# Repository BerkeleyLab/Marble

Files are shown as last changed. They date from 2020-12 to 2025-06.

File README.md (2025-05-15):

# Marble board

Marble is a dual FMC FPGA carrier board developed for general purpose use in particle accelerator electronics instrumentation. It is currently under development and the base platform for two accelerator projects at DOE: ALS-U (the Advanced Light Source Upgrade at LBNL) and LCLS-II HE (the Linac Coherent Light Source II High Energy upgrade).

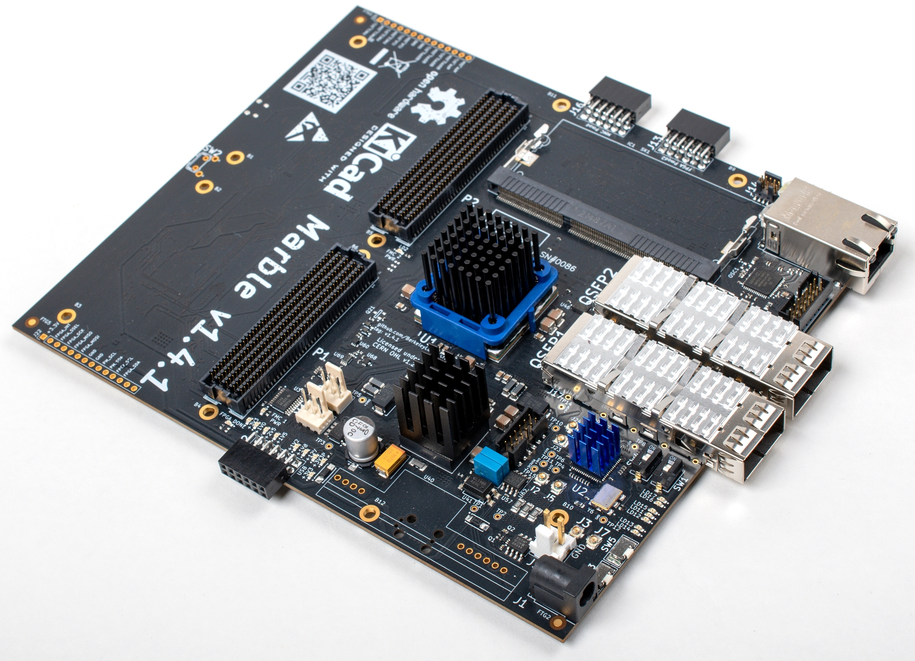
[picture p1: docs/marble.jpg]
marble

_Photo Credit: Thor Swift/LBNL_

The design responds to deployment needs in an accelerator environment: reliability, ability to be remotely programmed, safety watchdog, self monitoring, etc. It is intended to be the base digital design for instrumentation electronics, with the capability of connecting to different I/O or analog front ends through the FMC connectors. It targets cost-effectiveness for deployments of hundreds of units. It is based on a Network Attached Device (NAD) approach, where high-speed serial links serve as the communication backbone with other systems in the accelerator.

## Basic Idea

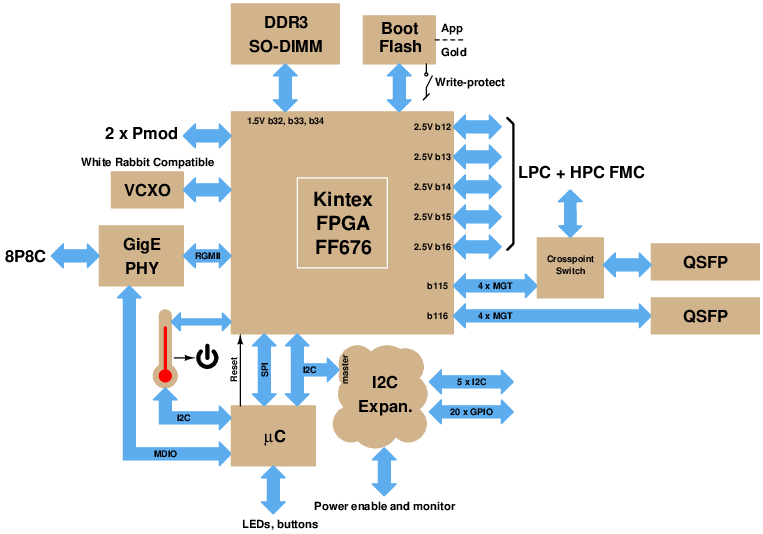
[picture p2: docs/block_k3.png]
block diagram


## Tools

The Marble design is fully Open Source (licensed under the CERN Open Hardware License v1.2) and designed using Open Source tools.

The schematic/layout tool used is [KiCad EDA](http://www.kicad.org/)
version 6.0.11; maybe you can use other versions in the 6.0.x series
(Marble design versions 1.3 and before used KiCad 5.0.x).
Other versions will very likely either not read the files
in this repo, or will save files that are not compatible with
collaborators' reference installations.
We also make use of [KiBoM](https://github.com/SchrodingersGat/KiBoM).

See more comments about KiCad versions in [design/scripts/README.md](design/scripts/README.md).

## Major Parts

* U1: Xilinx [XC7K160T-FFG676](https://www.xilinx.com/products/silicon-devices/fpga/kintex-7.html) FPGA
* SK1: 204-pin [DDR3](https://en.wikipedia.org/wiki/DDR3_SDRAM) [SO-DIMM](https://en.wikipedia.org/wiki/SO-DIMM)
* U54: ST [STM32F207VCT6](http://www.st.com/st-web-ui/static/active/en/resource/technical/document/datasheet/CD00237391.pdf) Microcontroller
* U4: Marvell [88E1512](https://www.marvell.com/documents/eoxwrbluvwybgxvagkkf/) Ethernet PHY
* U20: TI [CDCM61004](http://www.ti.com/product/CDCM61004) Clock Generator
* U23: FTDI [FT4232H-56Q](https://www.ftdichip.com/Products/ICs/FT4232H.htm) USB interface
* U35: Analog Devices [LTM4673](https://www.analog.com/en/products/ltm4673.html) Quad Output Voltage Regulator Module
* Y1: Taitien [TXEAADSANF-25.000000](https://www.taitien.com/wp-content/uploads/2015/12/XO-0076_TX.pdf) 25 MHz VCTCXO

## Documentation

Documentation is available in the [Marble documentation page](https://berkeleylab.github.io/Marble/manuals.html).

If you have a physical board that has already been tested you can jump directly to the User Guide. If you need to qualify, test, or troubleshoot a board, you can use the fabrication acceptance test guide. These documents are also available as artifacts for each fabrication release.

Other documentation includes notes on the board's [current measurement capabilities](docs/shunts.md).

## Manufacturing package and other scripted processes

The Marble design source files, along with documentation, are available in this repository under version control.
Other non-source artifacts (such as fabrication packages) are available for download for each manufactured release.
If you would like to manufacture Marble boards from any of the released version, download the manufacturing package for that particular version from the list of artifacts and request a quote from your favorite vendor. Marble is not yet available as a catalog item from any of our manufacturing partners.

When a new design version of Marble is ready for manufacture, a release is tagged in this repository and the corresponding artifacts are made available for download (e.g. manufacturing package, documentation, etc.). The physical boards have a [QR code](https://en.wikipedia.org/wiki/QR_code) on them, pointing to the board's tagged release on GitHub so a physical board can be mapped to the source code and fabrication package used for its manufacture.

Updating the QR code for a new release, updating the silkscreen design accordingly and generating a fabrication package is a process in itself. That and other processes are partially scripted. Additional information on those processes and the scripts used can be found in the [scripts subdirectory](design/scripts). A [README](design/scripts/README.md) covers the following:

* Inserting QR code on silkcsreen
* Generating artifacts for manufacturing
* Generating Xilinx constraint file
* Updating the I2C subsystem diagram in schematics

## Credits

The initial design work was supported by the Berkeley Accelerator Controls and Instrumentation (BACI), a DOE High Energy Physics (HEP) General Accelerator R&D (GARD) program and carried out by the Accelerator Technology Group (ATG) at LBNL, in collaboration with the Warsaw University of Technology (WUT) and Creotech Instruments in Poland.

The board was designed by Michal Gaska (WUT), and Larry Doolittle (LBNL) is the mastermind behind the design. Michael Betz, Vamsi Vytla, Sergio Paiagua, Eric Norum, Shree Murthy, and Keith Penney (LBNL) have also contributed to the design and supporting software and firmware throughout the development.

## Copyright

Marble Copyright (c) 2019-2023, The Regents of the University of California, through Lawrence Berkeley National Laboratory (subject to receipt of any required approvals from the U.S. Department of Energy). All rights reserved.

This documentation describes Marble and is licensed under the [CERN OHL v1.2](https://ohwr.org/project/licences/wikis/cern-ohl-v1.2).

NOTICE. This documentation was developed under funding from the U.S. Department of Energy and the U.S. Government consequently retains certain rights. As such, the U.S. Government has been granted for itself and others acting on its behalf a paid-up, nonexclusive, irrevocable, worldwide license in the documentation to reproduce, distribute copies to the public, prepare derivative works, and perform publicly and display publicly, and to permit others to do so.

You may redistribute and modify this documentation under the terms of the CERN OHL v.1.2. (http://ohwr.org/cernohl). THIS DOCUMENTATION IS PROVIDED BY THE COPYRIGHT HOLDERS AND CONTRIBUTORS "AS IS" AND ANY EXPRESS OR IMPLIED WARRANTIES, INCLUDING, BUT NOT LIMITED TO, THE IMPLIED WARRANTIES OF MERCHANTABILITY AND FITNESS FOR A PARTICULAR PURPOSE ARE DISCLAIMED. IN NO EVENT SHALL THE COPYRIGHT OWNER OR CONTRIBUTORS BE LIABLE FOR ANY DIRECT, INDIRECT, INCIDENTAL, SPECIAL, EXEMPLARY, OR CONSEQUENTIAL DAMAGES (INCLUDING, BUT NOT LIMITED TO, PROCUREMENT OF SUBSTITUTE GOODS OR SERVICES; LOSS OF USE, DATA, OR PROFITS; OR BUSINESS INTERRUPTION) HOWEVER CAUSED AND ON ANY THEORY OF LIABILITY, WHETHER IN CONTRACT, STRICT LIABILITY, OR TORT (INCLUDING NEGLIGENCE OR OTHERWISE) ARISING IN ANY WAY OUT OF THE USE OF THIS SOFTWARE, EVEN IF ADVISED OF THE POSSIBILITY OF SUCH DAMAGE. Please see the CERN OHL v.1.2 for applicable conditions.

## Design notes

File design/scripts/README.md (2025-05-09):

# Marble board scripting and processes

When a new design version of Marble is ready for manufacture, a release is tagged in this repository and the corresponding artifacts are made available for download (e.g. manufacturing package, documentation, etc.). We want the physical boards to have a [QR code](https://en.wikipedia.org/wiki/QR_code) on them, pointing to the board's tagged release on GitHub.  This way a physical board can be mapped to the source code and fabrication package that was used for its manufacture.

Updating the QR code for a new release, updating the silkscreen design accordingly and generating a fabrication package is a process in itself. That and other processes are partially scripted and documented here.

## Generating the manufacturing package

If you have made changes to the Marble design and are ready to generate the manufacturing package, the first step is to pick a version number for the new release. The current version is `v1.4.4`.

### Required software

* [KiCad](https://www.kicad.org/): version 6.0.x (x &ge; 9)
* [KiBoM](https://github.com/SchrodingersGat/KiBoM): version 1.9.1
* [KiAuto](https://github.com/INTI-CMNB/KiAuto): version 2.2.1

KiCad version 6 is needed.
We hope this still supports [reproducible](https://reproducible-builds.org) fabrication package builds. This means byte-for-byte identical zip files, independent of which person and computer runs the process.

### Update the QR code on the silkscreen

The QR code needs to be re-generated so it points to the new version release. To update the URL, edit the Python script used to generate the QR code image: `design/scripts/qr_create.py`. The URL in that file pointing to the current release is: <https://github.com/BerkeleyLab/Marble/releases/tag/v1.4.4>.

From the design directory, run the Python script:
```console
$ python scripts/qr_create.py
```
That will create a `mm_qr.png` file, which you should be able to preview and
scan with your phone to confirm it has the intended link.

Open the KiCad project: `design/Marble.kicad_pro`

Open the `Bitmap to Component Converter` clicking on this button at the top of the screen:

Bitmap to Component Converter

Click on `Load Bitmap` and select the `mm_qr.png` that you just generated with the Python script. Choose 400 x 400 DPI to get a 19.8 mm output size. Check the `Negative` and `Front silk screen`, click `Export to File` and select `logos/QR.kicad_mod` to replace the previous QR code with the new one. You can now close the `Bitmap to Component Converter` and insert the QR code into the silkscreen.

Open the `PCB Layout Editor` clicking on this button at the top of the screen:

Pcbnew

Press the `b` key to fill copper planes (completing connectivity and getting rid of rats-nest visual clutter), and unselect every layer on the right-hand side except for `F.Silkscreen`.  There's a nice "Hide All Layers" feature available by right-clicking on the layer list.

Select the QR code, right click and select `Update footprint...`. Click `Update` and `Close`.  Now you can check again with your phone, and save the design.

The above instructions are tested with KiCad 6.0.11. Be aware of KiCad issue [#6514](https://gitlab.com/kicad/code/kicad/-/issues/6514). If the results look corrupted and you are not able to scan the QR code from the PCB layout editor, select `Modern Toolset (Fallback)` under KiCad Preferences.

### Generate the manufacturing package

Now that you have the updated QR code on the silkscreen, we're ready to generate the manufacturing package. The process is summarized in the diagram below.

The current design does unfortunately have a baseline of four DRC errors:  overlapping courtyards of part pairs (U57, U62), (U32, U64), (U17, U63) and copper edge clearance for J10.
These are INA219 chips with two package options supported with two (overlapping) footprints.

From the `design` directory, run:

```console
$ bash scripts/manufacturing.sh
```

If everything worked out correctly, the script should have generated the fabrication package in a zipped archive containing the usual manufacturing files for both
PCB fabrication and turn-key assembly:
* Gerber
* Drill
* IPC-D-356
* Board stackup
* BoM
* X-Y placement
* Schematics

The above process is summarized in the diagram below.

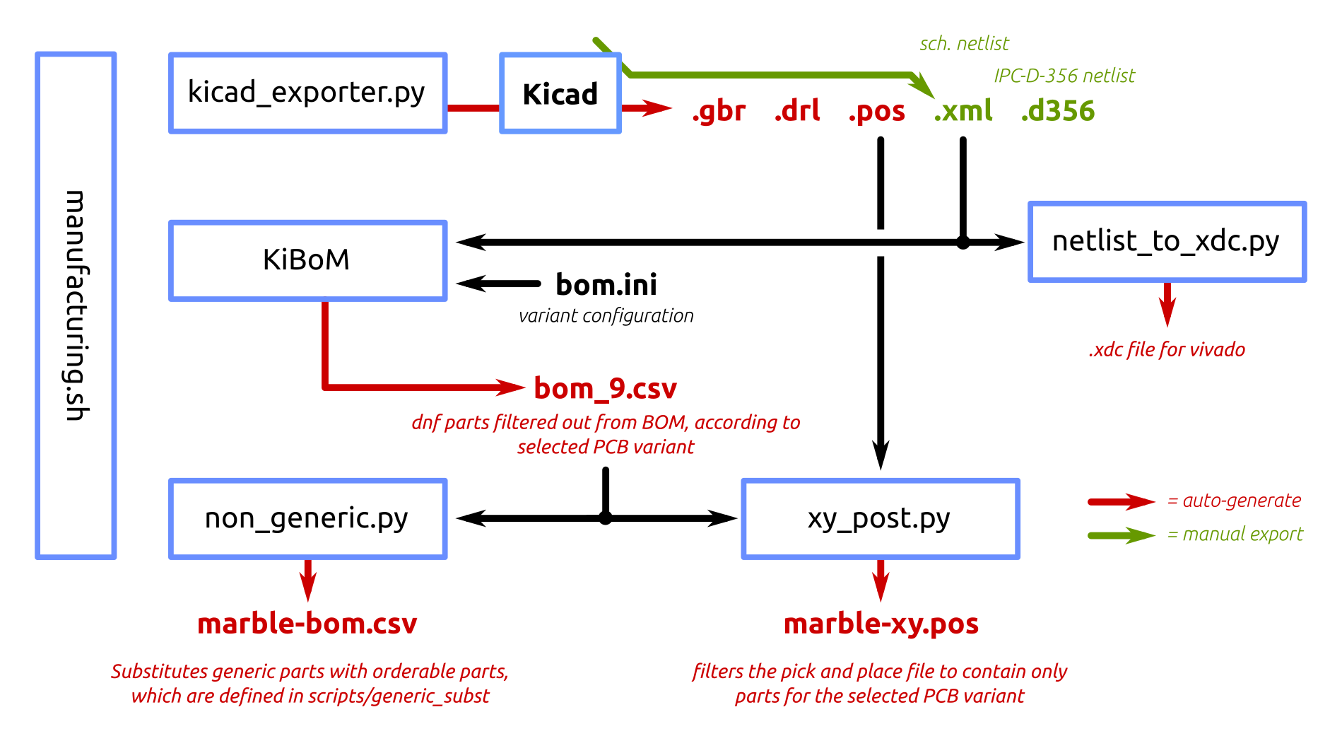
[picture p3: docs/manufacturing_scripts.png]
process


## Xilinx constraint file

A somewhat specialized tool is available to create an XDC file for the Marble design,
based on a netlist file exported from KiCad.

From KiCad (version 6.0.x), open the `Schematic Layout Editor` clicking on this button at the top of the screen:

Pcbnew

* From the top menu, select `File / Export /  Netlist`
* Select the `OrcadPCB2 tab`, click on `Export Netlist` and `Save`. The result shows up as `Marble.net`
* If the above netlist was saved in the `design` directory, from the command line run:
```console
$ python3 scripts/netlist_to_xdc.py Marble.net
```

The result shows up as `Marble.xdc`, which can be used for your FPGA designs.

## Update I2C subsystem diagram in schematics

Run the following command from the top level directory before importing the I2C subsystem diagram into the `I2C_MUX.sch` schematic:
```console
$ convert docs/marble2_i2c.eps -scale 1840 marble2_i2c.png
```
where `convert` is part of [ImageMagick](https://en.wikipedia.org/wiki/ImageMagick)
(Debian and derivatives: `apt-get install imagemagick`).

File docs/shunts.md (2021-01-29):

# Shunt resistors and current scaling

Three INA219 chips are used to monitor power supply currents
for +12V (nominal) busses on Marble.
Full-scale currents are programmable via the PG bits of the INA219
config register as shown in this table:

|               | INA219 config[12:11] |  FMC1     |  FMC2     |  main
| ------------- | -------------------- | --------- | --------- | ---------
| I2C address   |                      | 0x80      | 0x82      | 0x84
| INA219 refid  |                      | U17       | U32       | U57
| shunt value   |                      | 0.082 Ohm | 0.082 Ohm | 0.0273 Ohm
|               |   00  ( &pm; 40mV)   | 0.488 A   | 0.488 A   | 1.46 A
|               |   01  ( &pm; 80mV)   | 0.976 A   | 0.976 A   | 2.93 A
|               |   10  ( &pm; 160mV)  | 1.951 A   | 1.951 A   | 5.85 A
| (default)     |   11  ( &pm; 320mV)  | 3.902 A   | 3.902 A   | 11.71 A

Note that the first-run boards so far have 0.02 Ohm shunt resistors
for U17 and U32, which give pretty ridiculous values for
the current (full-scale) that the FMC spec says should be limited to 1A.
Also, the shunt for U57 there was 0.0227 Ohms.

Considerations that led to those resistor values were:

* General operations should use PG bits config[12:11] = 01
* Can turn range up or down by a factor of two for special use cases
* Full-scale 160 mV should not burn up the 1206 0.5W shunt resistor

Final answer, as shown above, and also used on the second batch of Marble-Mini:
82 mOhm Ohmite KDV12DR082ET (tripled for the main input shunt).

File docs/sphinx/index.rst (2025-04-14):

.. Marble documentation master file, created by
   sphinx-quickstart on Tue Apr  8 13:54:28 2025.
   You can adapt this file completely to your liking, but it should at least
   contain the root `toctree` directive.

Marble documentation
====================

Documentation for Marble board. The official development repository is
the `Marble Github Repository`_.

.. _`Marble Github Repository`: https://github.com/BerkeleyLab/Marble

.. toctree::
   :maxdepth: 2
   :caption: Contents:

   manuals

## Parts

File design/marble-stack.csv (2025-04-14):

Board Layer Stack
Number | Name | Type | Manufacturer | Material | Process | Thickness (mm) | Weight (oz) | Dk | Df | Orientation
 | Top Overlay | Overlay
 | Top Solder | Solder Mask | Altium Designer | SM-001 |  | 0,025 |  | 4 | 0,03
 | Top Surface Finish | Surface Finish |  | PbSn | HASL | 0,02
1 | Top Layer | Signal | Altium Designer | CF-004 | ED | 0,035 | 1 |  |  | Top
 | Dielectric 1 | Prepreg | Altium Designer | PP-013 |  | 0,11 |  | 4,3 | 0,02
2 | Int1 (GND) | Plane | Altium Designer | CF-004 | ED | 0,018 | 0,5
 | Dielectric 2 | Core | Altium Designer | Core-011 |  | 0,15 |  | 4,3 | 0,02
3 | Int2 (PWR) | Signal | Altium Designer | CF-004 | ED | 0,018 | 0,5 |  |  | Not allowed
 | Dielectric 3 | Prepreg | Altium Designer | PP-013 |  | 0,11 |  | 4,3 | 0,02
4 | Int3 (Sign) | Plane | Altium Designer | CF-004 | ED | 0,018 | 0,5
 | Dielectric 4 | Core | Altium Designer | Core-011 |  | 0,15 |  | 4,3 | 0,02
5 | Int4 (Sign) | Signal | Altium Designer | CF-004 | ED | 0,018 | 0,5 |  |  | Not allowed
 | Dielectric 5 | Prepreg | Altium Designer | PP-014 |  | 0,11 |  | 4,3 | 0,02
6 | Int5 (GND) | Plane | Altium Designer | CF-004 | ED | 0,018 | 0,5
 | Dielectric 6 | Core | Altium Designer | Core-011 |  | 0,15 |  | 4,3 | 0,02
7 | Int6 (PWR) | Plane | Altium Designer | CF-004 | ED | 0,018 | 0,5
 | Dielectric 7 | Prepreg | Altium Designer | PP-014 |  | 0,11 |  | 4,3 | 0,02
8 | Int7 (Sign) | Signal | Altium Designer | CF-004 | ED | 0,018 | 0,5 |  |  | Not allowed
 | Dielectric 8 | Core | Altium Designer | Core-011 |  | 0,15 |  | 4,3 | 0,02
9 | Int8 (Sign) | Plane | Altium Designer | CF-004 | ED | 0,018 | 0,5
 | Dielectric 9 | Prepreg | Altium Designer | PP-013 |  | 0,11 |  | 4,3 | 0,02
10 | Int9 (GND) | Signal | Altium Designer | CF-004 | ED | 0,018 | 0,5 |  |  | Not allowed
 | Dielectric 10 | Core | Altium Designer | Core-011 |  | 0,15 |  | 4,3 | 0,02
11 | Int10 (PWR) | Plane | Altium Designer | CF-004 | ED | 0,018 | 0,5
 | Dielectric 11 | Prepreg | Altium Designer | PP-013 |  | 0,11 |  | 4,3 | 0,02
12 | Bottom Layer | Signal | Altium Designer | CF-004 | ED | 0,035 | 1 |  |  | Bottom
 | Bottom Surface Finish | Surface Finish |  | PbSn | HASL | 0,02
 | Bottom Solder | Solder Mask | Altium Designer | SM-001 |  | 0,025 |  | 4 | 0,03
 | Bottom Overlay | Overlay
No back drills

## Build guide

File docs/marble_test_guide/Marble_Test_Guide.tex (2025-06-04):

\documentclass[12pt,oneside,a4]{article}
\usepackage{float}
\usepackage[utf8]{inputenc}
\usepackage[a4paper,width=160mm,top=25mm,bottom=25mm]{geometry}
\usepackage[lining,tabular]{fbb} % so math uses tabular lining figures
\usepackage{graphicx}
\usepackage{enumitem}
\usepackage{listings}
\usepackage[svgnames]{xcolor}
%\usepackage{background}

\setlist{leftmargin=*}
\usepackage{listings}
\lstset{basicstyle=\ttfamily,frame=single,xleftmargin=3em,xrightmargin=3em}
\usepackage[os=win]{menukeys}
\renewmenumacro{\keys}[+]{shadowedroundedkeys}
\usepackage{framed}
\usepackage{etoolbox}
\AtBeginEnvironment{leftbar}{\sffamily\small}
\usepackage{array,lipsum}
\newenvironment{fulltable}[1][H]
 {\begin{table}[#1]%
  \hspace*{-\leftmarginwidth}%
  \begin{minipage}{\fullwidth}}
 {\end{minipage}\end{table}}
\usetikzlibrary{chains,arrows,shapes,positioning}
\usepackage{hyperref}
\graphicspath{{figures/}} %Setting the graphicspath
\renewcommand\abstractname{Introduction}
%\backgroundsetup{contents=Not for v1.4.x}

\title{Marble -- Factory Acceptance Tests\\ \small{v1.4 2025}}

\begin{document}

\maketitle
\begin{center}
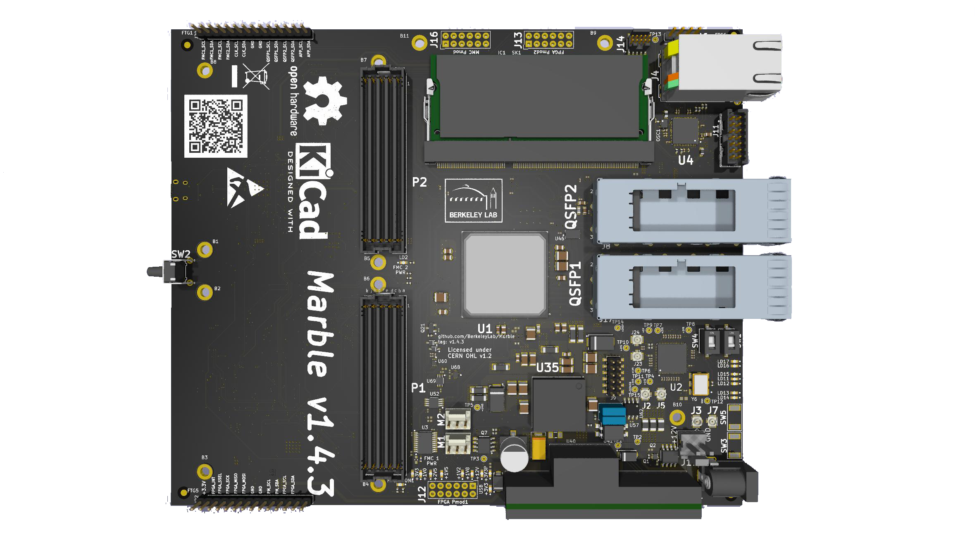
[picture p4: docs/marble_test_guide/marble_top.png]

\end{center}
\begin{abstract}
%\includegraphics[width=1.0\linewidth]{PhysLogger.png}\\
This document presents a user--friendly guide on how to perform Factory Acceptance Tests (FAT) for the Marble module. Tests begin from a short description of where Marble's useful connector, LED indicators, and test points are placed on the board. It is highly recommended to perform the tests in the order presented in this document.
\end{abstract}

\clearpage
\tableofcontents

\clearpage

\section{Overview}

\begin{leftbar}
Design files are open source and can be downloaded from GitHub:

https://github.com/BerkeleyLab/Marble
\end{leftbar}

\begin{leftbar}
Each board is marked with a revision number. Make sure that the

downloaded files correspond to your board.
\end{leftbar}

\subsection{Hardware requirements}
To perform all tests the following hardware is required:
\begin{enumerate}
    \item Lab bench-top power supply.
    \item Micro USB cable.
    \item QSFP loopback module.
    \item FMC Tester module.
    \item Multimeter.
    \item MMC JTAG (either SEGGER J-Link Mini or STMicroelectronics ST-Link V2).
    \item FPGA JTAG (example: Digilent JTAG HS3).
\end{enumerate}

\subsection{Software requirements}
To perform all tests the following software is required:
\begin{enumerate}
    \item Vivado 19.1.
    \item Serial port terminal. Example Miniterm, can be installed by:
	\begin{lstlisting}[backgroundcolor = \color{Gainsboro}, language=bash, frame=none]]
$ sudo apt-get install python3-serial
	\end{lstlisting}
	\item OpenOCD, can be installed by:
	\begin{lstlisting}[backgroundcolor = \color{Gainsboro}, language=bash, frame=none]]
$ sudo apt-get install openocd
	\end{lstlisting}
\end{enumerate}

\section{Power connection}\label{sec:Power_Connection}
Before connecting the power supply for the first time, it is highly recommended to verify that there are no shorts on the power rails.
First, use a multimeter set in resistance measurement mode to measure the resistance between metal pads of the \textbf{J19} connector (Figure \ref{fig:j19})
and ensure it is not electrically shorted (should not be <200 Ohms).

Next, measure the resistance between the power supply test points:

\begin{enumerate}
    \item \textbf{TP12 (GND)} and \textbf{TP7 (+2V0)}.
    \item \textbf{TP12 (GND)} and \textbf{TP9 (+1V0)}.
    \item \textbf{TP12 (GND)} and \textbf{TP10 (+2V5)}.
    \item \textbf{TP12 (GND)} and \textbf{TP8 (+1V8)}.
    \item \textbf{TP12 (GND)} and \textbf{TP6 (+1V5)}.
    \item \textbf{TP12 (GND)} and \textbf{TP4 (+1V2)}.
    \item \textbf{TP12 (GND)} and \textbf{TP11 (+3V3)}.
    \item \textbf{TP12 (GND)} and \textbf{TP15 (+3V3USB)}.
    \item \textbf{TP12 (GND)} and \textbf{TP14 (+3V3P)}.
    \item \textbf{TP12 (GND)} and \textbf{TP5 (+1V05)}.
\end{enumerate}

\begin{figure}[H]
\begin{center}
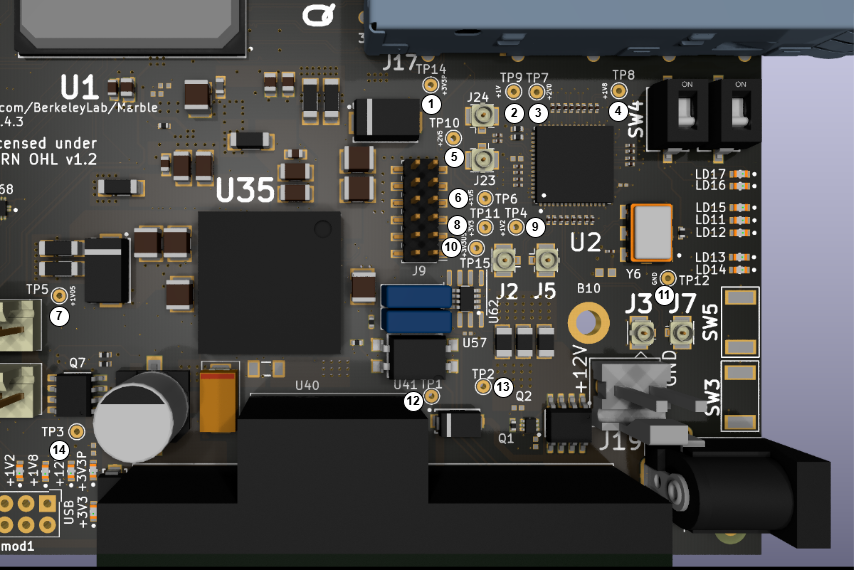
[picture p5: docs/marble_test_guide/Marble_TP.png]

 \caption{Test points. }\label{tp}
\end{center}
\end{figure}

\begin{figure}[H]
\begin{center}
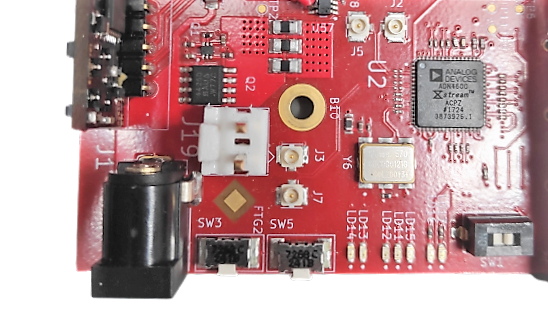
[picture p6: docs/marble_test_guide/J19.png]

 \caption{Connector's terminals. }\label{fig:j19}
\end{center}
\end{figure}
\begin{leftbar}
Measured resistance should be around \textbf{{\color{red}200 kOhm}}
\end{leftbar}

It is also highly recommended at this point to attach silicone feet (bumpers) to the bottom of the board to avoid
both mechanical component damage in general and short circuits if resting on a conductive surface.
See \texttt{doc/README\_fab.txt} for details.

If the resistance is correct, connect the main power. For this purpose, the current limitation on the power supply should be set to 100\thinspace mA and the voltage to \hbox{12\thinspace V}. \textbf{Make sure that the current limit of the laboratory power supply is on.} Now the power cable can be connected to the board and the used laboratory power supply channel can be switched on.
This should result in the \textit{3.3V} and \textit{12V} LEDs lighting up as shown on Figure \ref{fig:12V_led}. Now it is recommended to go to section \nameref{microcontroller}.
\begin{figure}[H]
\begin{center}
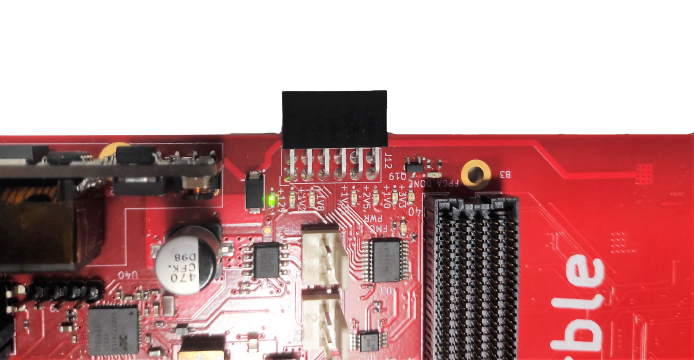
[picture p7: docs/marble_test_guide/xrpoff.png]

 \caption{12V indicator LED is on. }\label{fig:12V_led}
\end{center}
\end{figure}

\section{Microcontroller Programming}
\label{microcontroller}

Download the latest version of the microcontroller testing code from GitHub:
\begin{leftbar}
https://github.com/BerkeleyLab/Marble-MMC
\end{leftbar}

A recent version of OpenOCD (v0.10.0 or later) is required.
\begin{enumerate}
	\item Connect JTAG module to \textbf{J14} as shown on Figure \ref{fig:j14}.
	\item Connect the micro USB cable and using the serial terminal, connect to the last serial port for the new listed device in the operating system. Use 115200 baudrate.
	\item Power up the board.
	\item Program the microcontroller using the following commands:
	\begin{enumerate}
	\item Go to the main folder of the downloaded repository.
	\item From the command line, run the following:
	\begin{lstlisting}[backgroundcolor = \color{Gainsboro}, language=bash, frame=none]]
$ make marble_download
	\end{lstlisting}
	\end{enumerate}
\item After successful programming, a menu in the serial terminal should appear and LEDs (\textbf{LD15}, \textbf{LD11}, \textbf{LD12}) should blink.
\end{enumerate}

\begin{figure}[H]
\begin{center}
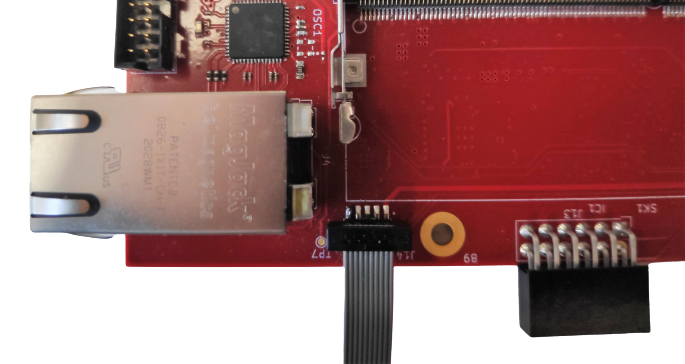
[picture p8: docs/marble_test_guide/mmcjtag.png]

 \caption{J14 connector. }\label{fig:j14}
\end{center}
\end{figure}

\section{Power Supply Programming}

\textbf{Warning:} Only perform the following steps if there are no shorts on the power rails (see section \ref{sec:Power_Connection}).

\begin{enumerate}
    \item Connect the micro USB cable and note the serial device name assigned to it (i.e. /dev/ttyUSB3).  It will always be the last port of a group of 4 associated with the Marble's FT4232 USB-to-UART.
    \item Set up voltage to 12\thinspace V and the current limit to 1\thinspace A on a lab power supply.
    \item Power up the board.
    \item Open a terminal in the Marble-MMC repository downloaded in section 3.
    \item Run the LTM4673 programming script (where \$TTY is the serial device name noted above):
      \begin{lstlisting}[backgroundcolor = \color{Gainsboro}, language=bash, frame=none]]
$ sh scripts/program_ltm4673.sh $TTY -f LTM4673_reglist.txt -s
      \end{lstlisting}
    \item Power cycle by turning the lab power supply Off and then On.
    \item All power LED indicators should be On (Figure \ref{fig:leds}).
    \item Using multimeter measure the voltage between the test points:
    \begin{enumerate}
	\item \textbf{TP12 (GND)} and \textbf{TP7 (+2V0)} - expected voltage: +2.0\thinspace V.
	\item \textbf{TP12 (GND)} and \textbf{TP9 (+1V0)} - expected voltage: +1.0\thinspace V.
	\item \textbf{TP12 (GND)} and \textbf{TP10 (+2V5)} - expected voltage: +2.5\thinspace V.
	\item \textbf{TP12 (GND)} and \textbf{TP8 (+1V8)} - expected voltage: +1.8\thinspace V.
	\item \textbf{TP12 (GND)} and \textbf{TP6 (+1V5)} - expected voltage: +1.5\thinspace V.
	\item \textbf{TP12 (GND)} and \textbf{TP4 (+1V2)} - expected voltage: +1.2\thinspace V.
	\item \textbf{TP12 (GND)} and \textbf{TP11 (+3V3)} - expected voltage: +3.3\thinspace V.
	\item \textbf{TP12 (GND)} and \textbf{TP15 (+3V3USB)} - expected voltage: +3.3\thinspace V.
	\item \textbf{TP12 (GND)} and \textbf{TP14 (+3V3P)} - expected voltage: +3.3\thinspace V.
	\item \textbf{TP12 (GND)} and \textbf{TP5 (+1V05)} - expected voltage: +1.05\thinspace V.
\end{enumerate}
\end{enumerate}

\begin{figure}[H]
\begin{center}
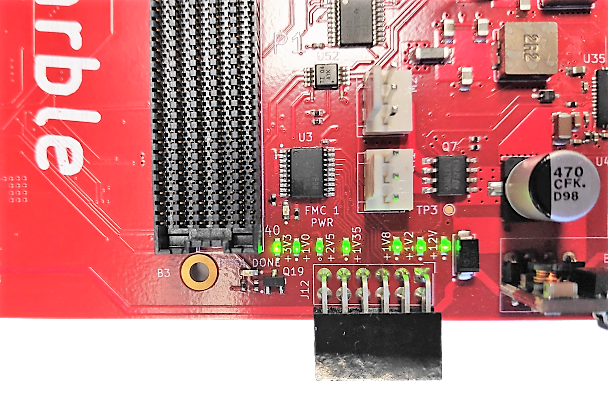
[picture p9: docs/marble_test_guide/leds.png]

 \caption{Power LED indicators after a successful power cycle.}\label{fig:leds}
\end{center}
\end{figure}

\section{FPGA Programming}
Download the latest version of the FPGA testing code from GitHub:
\begin{leftbar}
https://github.com/BerkeleyLab/Bedrock/
\end{leftbar}

\begin{leftbar}
Before testing the FPGA it is recommended to set up the current limit to 2A on the lab power supply.
\end{leftbar}
\subsection{FMC test}
\begin{leftbar}
Board power should be turned off when inserting and removing the FMC module.
\end{leftbar}
\begin{enumerate}
	\item Plug FMC Tester module to one of the FMC connectors as shown on Figure \ref{fig:FMC_tester}.
	\item Connect the micro USB cable and, using the serial terminal, connect to the last serial port for the new device listed in the operating system. Use 115200 baudrate.
	\item Change the network adapter settings to connect with static IP address \textbf{192.168.9.10}.
	\item Connect Marble to the computer using an Ethernet cable.
	\item Power up the board.
	\item In the serial terminal menu choose \menu{4) GPIO control
>A) FMC power} to turn on power to the FMCs.
	\item Program the FPGA using the following steps:
	\begin{enumerate}
	\item Go to the folder \textbf{Bedrock/projects/test\_marble\_family/}
	\item Open command terminal and run command:
	\begin{lstlisting}[backgroundcolor = \color{Gainsboro}, language=bash, frame=none]]
$ mutil usb
	\end{lstlisting}
	\end{enumerate}
	\item To run a test do the following steps:
	\begin{enumerate}
	\item Go to the folder \textbf{Bedrock/projects/test\_marble\_family/}
	\item To test P1 FMC connector run the following command:
	\begin{lstlisting}[backgroundcolor = \color{Gainsboro}, language=bash, frame=none]]
$ PYTHONPATH=../../badger:../../periphera\l_drivers
/i2cbridge python fmc\_test\_c.py --ip $IP --fmc 0
	\end{lstlisting}
	\item To test P2 FMC connector run the following command:
	\begin{lstlisting}[backgroundcolor = \color{Gainsboro}, language=bash, frame=none]]
$ PYTHONPATH=../../badger:../../periphera\l_drivers
/i2cbridge python fmc\_test\_c.py --ip $IP --fmc 1
	\end{lstlisting}
	\end{enumerate}
\end{enumerate}

\begin{figure}[H]
\begin{center}
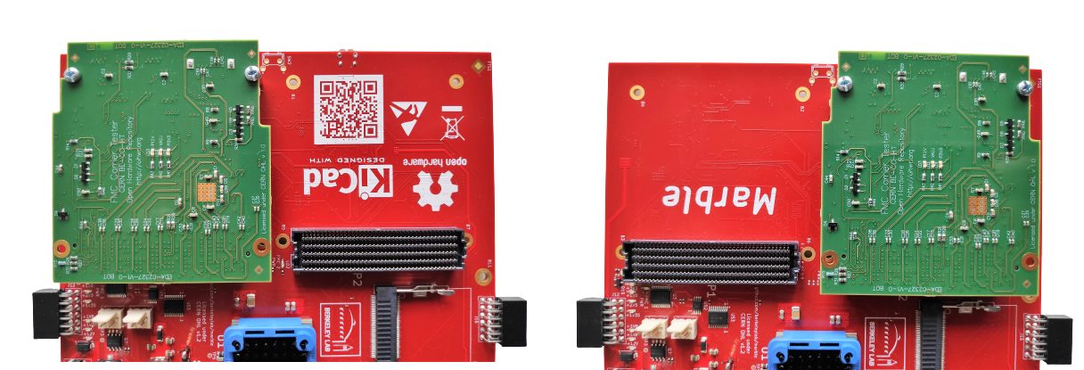
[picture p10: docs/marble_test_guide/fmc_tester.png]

  \caption{FMC connectors FMC Tester board plugged in.}\label{fig:FMC_tester}
\end{center}
\end{figure}

\subsection{QSFP test}

\begin{leftbar}
Board power should be turned off when inserting and removing the QSFP module.
\end{leftbar}
\begin{enumerate}
	\item Plug QSFP loopback module to one of the ports.
	\item Connect FPGA JTAG programmer.
	\item Configure FPGA using \texttt{marble\_ibert.bit} bit file.
	\begin{enumerate}
		\item Run Vivado
		\item Go to \menu{Flow>Open Hardware Manager} and then \menu{Tools>Auto Connect}
		\item Click \menu{Tools>Program Device>xc7k160t\_0} to open the programming window.
		\item Choose the \textit{bitstream file} and click \menu{Program}
	\end{enumerate}
	\item After successful programming, the Dashboard should start automatically.
	\item Detect links by clicking \menu{Serial I/O Links>Auto-detect links}
	\item Correctly detected and working links should appear as shown in figure \ref{fig:links}.
	\item Connect the QSFP loopback module to the other QSFP connector and repeat the steps above.
\end{enumerate}

\begin{figure}[H]
\begin{center}
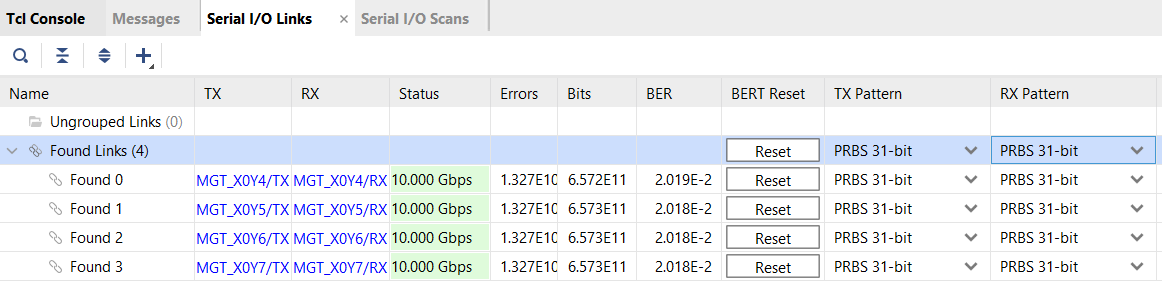
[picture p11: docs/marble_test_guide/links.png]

 \caption{Working links.}\label{fig:links}
\end{center}
\end{figure}

\subsection{Ethernet test}
The following steps should be performed to test the Ethernet:
\begin{enumerate}
    \item Program the FPGA using the following steps:
	\begin{enumerate}
	\item Go to the folder \textbf{Bedrock/projects/test\_marble\_family/}
	\item Open command terminal and run command:
	\begin{lstlisting}[backgroundcolor = \color{Gainsboro}, language=bash, frame=none]]
$ mutil usb
	\end{lstlisting}
	\end{enumerate}
    \item Change the network adapter settings to connect with static IP address \textbf{192.168.9.10}.
    \item Connect Marble to the computer using an Ethernet cable.
    \item Ping the board:
    \begin{lstlisting}[backgroundcolor = \color{Gainsboro}, language=bash, frame=none]]
$ ping 192.168.9.10
	\end{lstlisting}
    \item Expected result:
    \begin{lstlisting}[backgroundcolor = \color{Gainsboro}, language=bash, frame=none]]
Pinging [192.168.9.10] with 32 bytes of data:
Reply from 192.168.9.10: bytes=32 time=17ms TTL=55
Reply from 192.168.9.10: bytes=32 time=152ms TTL=55
Reply from 192.168.9.10: bytes=32 time=12ms TTL=55
Reply from 192.168.9.10: bytes=32 time=14ms TTL=55

Ping statistics for 192.168.9.10:
    Packets: Sent = 4, Received = 4, Lost = 0 (0% loss),
Approximate round trip times in milli-seconds:
    Minimum = 12ms, Maximum = 152ms, Average = 48ms
	\end{lstlisting}
    \item For data traffic test use \textit{iperf}. Run command:
    \begin{lstlisting}[backgroundcolor = \color{Gainsboro}, language=bash, frame=none]]
$ iperf -c 192.168.9.10 -u -b 1000M -p 802
	\end{lstlisting}
\end{enumerate}

\section{Appendix}
\subsection{An alternative way to program FPGA}
Programming FPGA using Vivado and Digilent JTAG HS3:
\begin{enumerate}
		\item Run Vivado
		\item Go to \menu{Flow>Open Hardware Manager} and then \menu{Tools>Auto Connect}
		\item Click \menu{Tools>Program Device>xc7k160t\_0} to open the programming window.
		\item Choose the \textit{bitstream file} and click \menu{Program}

	\item After successful programming, the Dashboard should start automatically.
\end{enumerate}
\end{document}

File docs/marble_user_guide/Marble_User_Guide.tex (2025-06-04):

\documentclass[12pt,oneside,a4]{article}
\usepackage{float}
\usepackage[utf8]{inputenc}
\usepackage[a4paper,width=160mm,top=25mm,bottom=25mm]{geometry}
\usepackage[lining,tabular]{fbb} % so math uses tabular lining figures
\usepackage{graphicx}
\usepackage{enumitem}
\usepackage{listings}
\usepackage[svgnames]{xcolor}
\usepackage{subfig}
\usepackage{booktabs}
\usepackage{multirow}
\usepackage{svg}
\usepackage{tabu}
\usepackage{ltablex}
\usepackage{longtable}

\setlist{leftmargin=*}
\usepackage{listings}
\lstset{basicstyle=\ttfamily,frame=single,xleftmargin=3em,xrightmargin=3em}
\usepackage[os=win]{menukeys}
\renewmenumacro{\keys}[+]{shadowedroundedkeys}
\usepackage{framed}
\usepackage{etoolbox}
\AtBeginEnvironment{leftbar}{\sffamily\small}
\usepackage{array,lipsum}
\newenvironment{fulltable}[1][H]
 {\begin{table}[#1]%
  \hspace*{-\leftmarginwidth}%
  \begin{minipage}{\fullwidth}}
 {\end{minipage}\end{table}}
\usetikzlibrary{chains,arrows,shapes,positioning}
\usepackage{hyperref}
\graphicspath{{figures/}} %Setting the graphicspath
\renewcommand\abstractname{Introduction}

\title{Marble -- User Guide\\ \small{v1.4 2025}}
\author{}

\begin{document}

\maketitle
\begin{center}

\end{center}
\begin{abstract}
%\includegraphics[width=1.0\linewidth]{PhysLogger.png}\\
Marble is a fully open source dual FMC carrier board designed for the Accelerator Technologies Group of the Engineering Division of Lawrence Berkeley National Laboratory. This document presents the technical documentation of the Marble module divided into individual functional sections.
Design files are made in KiCad 6 and are licensed under the CERN OHL \hbox{v.~1.2}.
This guide primarily applies to Marble v1.4.x.
\end{abstract}

\clearpage
\tableofcontents

\clearpage

\section{Overview}

Design files are open source and can be downloaded from GitHub:

\begin{leftbar}
\url{https://github.com/BerkeleyLab/Marble}
\end{leftbar}

Marble is a dual FMC carrier module based on an Kintex-7 FPGA. The block diagram of the module is shown in figure \ref{fig:block}.

\begin{figure}[H]
\begin{center}
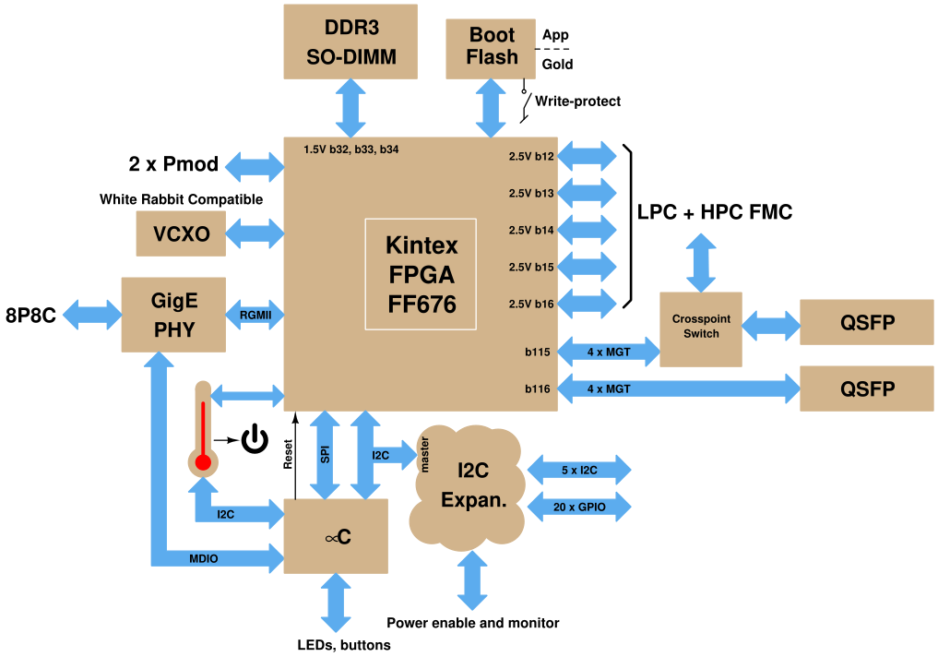
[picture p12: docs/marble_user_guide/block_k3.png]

 \caption{Marble block diagram.}\label{fig:block}
\end{center}
\end{figure}

Supporting FPGA code can be found in LBNL's Bedrock project

\begin{leftbar}
\url{https://github.com/BerkeleyLab/Bedrock}
\end{leftbar}

and microcontroller code in LBNL's Marble-MMC project

\begin{leftbar}
\url{https://github.com/BerkeleyLab/Marble-MMC}
\end{leftbar}

While you are not required to use those code bases, they are useful for
getting started, and some of this document assumes that you use them,
or at least code based on them.

\begin{figure}[H]
\begin{center}
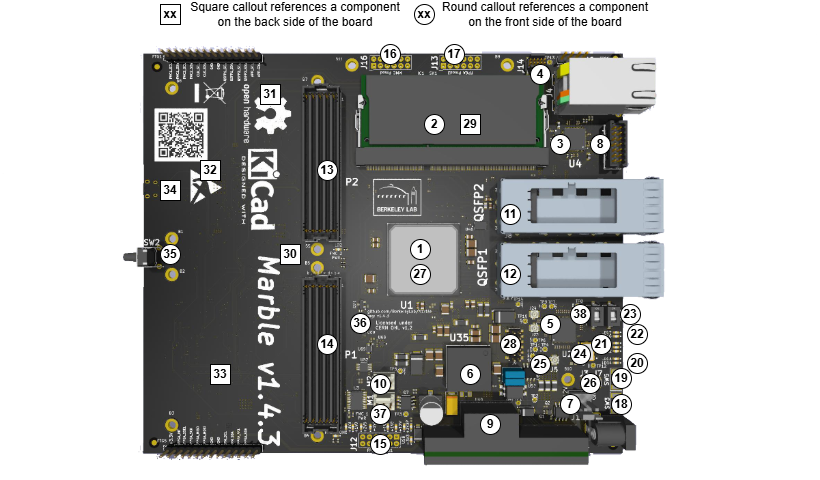
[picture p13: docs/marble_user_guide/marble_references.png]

 \caption{Marble board components.}\label{fig:components}
\end{center}
\end{figure}

\begin{longtable}[htbp]{@{}ccp{0.4\linewidth}p{0.3\linewidth}}
\toprule
\textbf{Callout} &
  \textbf{\begin{tabular}[c]{@{}c@{}}Reference\\ Designator\end{tabular}} &
  \textbf{Component Description} &
  \textbf{Notes} \\ \midrule
1  & U1  & FPGA Xilinx Kintex-7      & XC7K160T-2FFG676C \\
2  & SK1 & DD3 SO-DIMM memory module & VR7PU286458FBAMJT \\
3  & U4  & 10/100/1000 Ethernet PHY  & 88E1512-A0-NNP2I000  \\
4  & J14, J6 & Microcontroller programming connectors         &  \\
5  & U2  & 8x8 Clock Crosspoint Switch   & ADN4600ACPZ     \\
6  & U35 & Power Management          & LTM4673IY\#PBF   \\
7  & J1, J19 & 12V power input       & FC68148(DC-10A), 641119-2  \\
8  & J11 & FPGA JTAG connector       & 87831-1420   \\
9  & U40 & PoE module (optional)     & AG5300          \\
10 & M1, M2 & 3-pin PC fan connectors & SWR25X-NRTC-S03-ST-BA \\
11 & J8  & QSFP connector            & QSFP8-038-01-L-D-RA1 \\
12 & J17 & QSFP connector            & QSFP8-038-01-L-D-RA1   \\
13 & P2  & FMC HPC connector         & ASP-134486-01 \\
14 & P1  & FMC HPC connector         & ASP-134486-01     \\
15 & J12 & Pmod connected to FPGA    & PPTC062LJBN-RC     \\
16 & J16 & Pmod connected to microcontroller  & PPTC062LJBN-RC    \\
17 & J13 & Pmod connected to FPGA    & PPTC062LJBN-RC    \\
18 & SW3 & User button connected to microcontroller      &  KSS241GLFS  \\
19 & SW5 & FPGA reset button         & KSS241GLFS      \\
20 & LD13, LD14 & User LEDs connected to shared I2C bus & KPH-1608CGCK \\
21 & LD11-12, LD15 & User LEDs connected to microcontroller &  KPH-1608CGCK  \\
22 & LD16, LD17    & User LEDs connected to FPGA &  KPH-1608CGCK     \\
23 & SW1 & Memory write protection switch  & A6SN-1101 \\
24 & Y6  & 10-280MHz Clock generator   & SI570  \\
25 & J2, J5    & External clock source input & U.FL      \\
26 & J3, J7 &  External clock source input &   U.FL       \\
27 & U44-U50    & GTX Transceivers Mux & PI3DBS12212AZBSEX  \\
28 & J9  & Power Management programming header & 0.1 inch male 4-pin header \\
29 & Y1-Y3, U20 & Internal 125 MHz \& 20MHz clock sources & CDCM61004RHBT \\
30 & U30 &  FPGA SPI flash memory  & S25FL128SAGMFIR01 \\
31 & U5  &  I2C multiplexer    & TCA9548ARGER   \\
32 & U23 &  USB bridge: UART and JTAG & FT4232H-56Q   \\
33 & U54 & Housekeeping Microcontroller  & STM32F207VCTx  \\
34 & J10 & Micro USB connector for U23  & 10103594-0001LF  \\
35 & SW2 & \textcolor{red}{Not populated user button (physically connected to SW3)}  & SKHHLQA010  \\
36 & U60 & Over-voltage and Under-voltage Reset IC & TPS3703A7330DSERQ1 \\
37 & LD4-10, LD18-19 & Power rails indicator LEDs & KPH-1608CGCK \\ \bottomrule

\caption{}
\label{tab:callouts}
\end{longtable}

The board has the following functionalities and features:
\begin{enumerate}
	\item Xilinx Kintex-7 FPGA XC7K160T-2FFG676C
	\item Supports FPGA golden image
	\item Housekeeping microcontroller (Module Management Controller) with UART console
	\item DDR3 204-SODIMM memory module connector. The board supports up to 4 GB memory.
	\item Two FMC HPC connectors, but not all signals are connected to the FPGA.
	\item 1Gb Ethernet with PoE
	\item Built-in clock generator that supports White Rabbit synchronization
	\item Various input clock configurations
	\item Two QSFP cages that support data transfer up to 40 Gb/s each
	\item Built-in USB JTAG which works with OpenOCD
\end{enumerate}

\begin{table}[htbp]
\centering
\begin{tabular}{@{}lcl@{}}
\toprule
FPGA Bank  & Bank Power Supply & Description \\ \midrule
Bank 12 HR & +2.5V             & FMC2 LA 00-16 (plus SPI, Self JTAG) \\
Bank 13 HR & +2.5V             & FMC2 HA\\
Bank 14 HR & +2.5V             & FMC2 LA 17-33 (plus config, Pmod)\\
Bank 15 HR & +2.5V             & FMC1 LA 00-16 (plus I2C, UART, Pmod)\\
Bank 16 HR & +2.5V             & FMC1 LA 17-33 (plus RGMII)\\
Bank 32 HP & +1.5V             & DDR3        \\
Bank 33 HP & +1.5V             & DDR3 (plus Pmod, White Rabbit) \\
Bank 34 HP & +1.5V             & DDR3       \\ \bottomrule
\end{tabular}
\caption{}
\label{tab:banks}
\end{table}

\subsection{Configuration Memory}\label{sec:Overview:Configuration}

A 16 Mbyte SPI flash memory chip (Infineon S25FL128SAGMFIR01) is directly connected to the FPGA,
and the FPGA is configured with M[2:0] = 001 for Master SPI Mode.
The configuration is automatically loaded from the lowest address of flash memory after a power cycle or reset.
The board is equipped with a switch (fig \ref{fig:bootsw}) that can block the programming of the configuration memory.
When the switch is in the ON position, Write Protection is enabled. WP signal status can be read via I2C IO expander.
This write-protect feature is a key part of the board's `unbrickable' feature.

To write to configuration memory the first time, an FPGA image must be loaded some other way
(on-board USB JTAG, or external JTAG pod on J11).
That image then acts as a bridge between the host computer and the flash IC over its SPI interface,
allowing a ``golden image'' to be written to flash (with the WP switch OFF).
An example implementation of such a bridge (from Ethernet) is provided in Bedrock.
See its {\tt badger/spi\_flash.v} and {\tt badger/tests/spi\_test.py} files.
The default Marble image (built in its\hfil\break
{\tt projects/test\_marble\_family} directory)
provides this interface on Ethernet port 804 for configuration memory programming.

\begin{figure}[H]
\begin{center}
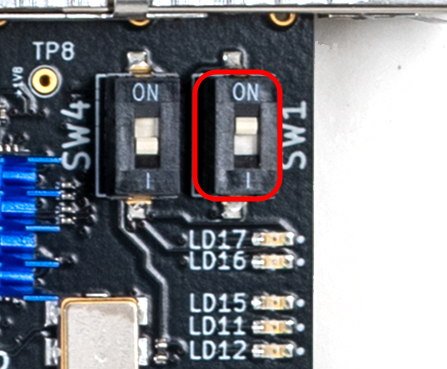
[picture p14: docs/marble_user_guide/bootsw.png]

 \caption{Memory write protection switch.}\label{fig:bootsw}
\end{center}
\end{figure}

\subsection{FPGA reset}
During power system startup, the U60 chip keeps the PROGRAM\_B signal low. When a valid supply voltage is detected on the last power-up sequence, U60 changes state on the PROGRAM\_B signal which causes the configuration file to be loaded from flash memory.

A local operator can reset the FPGA manually using the SW5 button. Additionally, the MMC can reset the FPGA.

\subsection{JTAG}
There are 3 sources of JTAG for FPGA:
\begin{enumerate}
	\item external JTAG (highest priority)
	\item internal USB-JTAG (middle priority)
	\item self JTAG (lowest priority)
\end{enumerate}

\subsubsection{External JTAG}
When the external JTAG is connected to J11, GNDDetect signal from the connector switches the multiplexer to pass JTAG signals from the connector to the FPGA.  After unplugging cable, the GNDDetect signal is not present and the multiplexer connects internal USB-JTAG to FPGA.

When external JTAG is connected, any other JTAG sources are not available.

\subsubsection{Internal USB-JTAG}
Internal USB-JTAG is done by using the first data channel of FT4232, which can work as a JTAG. When the micro USB cable is connected, +5V
from USB bus switches the multiplexer to pass data from FT4232 to FPGA.

\subsubsection{Self-JTAG}
Internal self-JTAG can be used only when USB cable and external JTAG are not connected. In this configuration FPGA JTAG signals are connected to FPGA Bank 12.
Self-JTAG has not been tested; no known bitfiles or software supports it.

\begin{table}[htbp]
\centering
\begin{tabular}{@{}ccc@{}}
\toprule
Signal name& Self JTAG signal & FPGA pin \\ \midrule
JTAG TDI & Self\_FPGA\_TDI & IO\_L10P \\
JTAG TCK & Self\_FPGA\_TCK & IO\_L10N \\
JTAG TMS & Self\_FPGA\_TMS & IO\_L20P \\
JTAG TDO & Self\_FPGA\_TDO & IO\_L20N \\ \bottomrule
\end{tabular}
\caption{}
\label{tab:selfjtag}
\end{table}

\subsection{LEDs}
Two general purpose LEDs are directly connected to the FPGA chip:
\begin{enumerate}
	\item LD16 - connected to pin IO\_L18P\_33
	\item LD17 - connected to pin IO\_25\_33
\end{enumerate}

\subsection{FPGA Programming}
A reference design with a constraint file, ready for synthesis with Vivado 2020.2 or newer,
can be found here:
\begin{leftbar}
\url{https://github.com/BerkeleyLab/Bedrock}
\end{leftbar}
With your build environment setup according to the documentation in Bedrock's\hfil\break
{\tt dependencies.txt}, a bitfile can be built with:
	\begin{lstlisting}[backgroundcolor = \color{Gainsboro}, language=bash, frame=none]
$ cd projects/test_marble_family
$ make marble2.bit
	\end{lstlisting}

\subsubsection{Internal JTAG}

\begin{leftbar}
Before testing the FPGA, it is recommended to set up the current limit to 2\thinspace A on the lab power supply.
\end{leftbar}

The easiest way to program the FPGA the first time is with the following steps:
\begin{enumerate}
	\item Attach the Marble board to your workstation with a micro USB cable to J10
	\item Go to the Bedrock directory {\tt projects/test\_marble\_family}
	\item Open command terminal and run command:
	\begin{lstlisting}[backgroundcolor = \color{Gainsboro}, language=bash, frame=none]]
$ BITFILE=marble2.$GITID.bit ./mutil usb
	\end{lstlisting}
	\item After the successful programming, LEDs LD16 and LD17 should blink alternately.
\end{enumerate}

\subsubsection{External JTAG}
Programming FPGA using Vivado and Digilent JTAG HS3 connected to J11:
\begin{enumerate}
		\item Run Vivado
		\item Go to \menu{Flow>Open Hardware Manager} and then  \menu{Tools>Auto Connect}
		\item Click \menu{Tools>Program Device>xc7k160t\_0} to open the programming window.
		\item Choose the \textit{bitstream file} and click \menu{Program}
		\item After the successful programming, LEDs LD16 and LD17 should blink alternately.
\end{enumerate}

\section{SO-DIMM}

The size of the DDR3 memory can be determined by the user by assembling the appropriate SO-DIMM module to the board. The use of a 204 pin SO-DIMM connector allows up to 4 GB of RAM to be connected to the FPGA. An I2C interface is provided to the memory module so that additional information about the module can be read. The default power supply for memory and HP banks is set to 1.5V and can only be changed by changing resistors. ECC is not supported by the module.\\

A reference design with a memory controller and a constraint file can be found here:
\begin{leftbar}
\url{https://github.com/enjoy-digital/litex}
\end{leftbar}
Bedrock's CI process has a job (marble\_ddr3\_test) that uses LiteX to build a valid bitfile.
You can follow along by peeking in .gitlab/ci/oscope.gitlab-ci.yml.

\section{GTX Routing}
Gigabit transceivers routing can be configured by the microcontroller. Transceivers from Bank 116 are permanently connected to module QSFP1. Transceivers from Bank 115 can be routed in 3 ways:
\begin{enumerate}
    \item 4 transceivers connected to QSFP2
    \item 4 transceivers connected to FMC P2
    \item 2 transceivers connected to FMC P2 and 2 transceivers connected to FMC P1
\end{enumerate}

Transceiver routing configuration is controlled by the microcontroller via control of three select signals to onboard gigabit multiplexers.
To query or set the routing multiplexers' state, use the UART console or the MMC's mailbox interface to the FPGA (see section \ref{sec:MMC:Mailbox}).
Three signals control the multiplexers which provide high quality signal switching.
By default, the multiplexers are set to route signals to the second QSFP connector.
In the table \ref{tab:gtx_routing}, the MUXx columns correspond to the controlling logical state.

% Please add the following required packages to your document preamble:
% \usepackage{booktabs}
\begin{table}[htbp]
\begin{tabular}{@{}llllllll@{}}
\toprule
 & MUX3 & MUX2 & MUX1 & MGT4       & MGT5       & MGT6       & MGT7      \\ \midrule
 & 0    & 0    & 0    & FCM2-DP0   & FMC2-DP1   & FMC2-DP2   & FMC1-DP1  \\
 & 0    & 0    & 1    & FCM2-DP0   & FMC2-DP1   & FMC1-DP0   & FMC1-DP1  \\
 & 0    & 1    & 0    & FCM2-DP0   & FMC2-DP1   & FMC2-DP2   & FMC2-DP3  \\
 & 0    & 1    & 1    & FCM2-DP0   & FMC2-DP1   & FMC1-DP0   & FMC2-DP3  \\
 & 1    & X    & X    & QSFP2:3/10 & QSFP2:1/12 & QSFP2:2/11 & QSFP2:4/9 \\ \bottomrule
\end{tabular}
\caption{GTX transceivers routing table}\label{tab:gtx_routing}
\end{table}

\begin{figure}[H]
\begin{center}
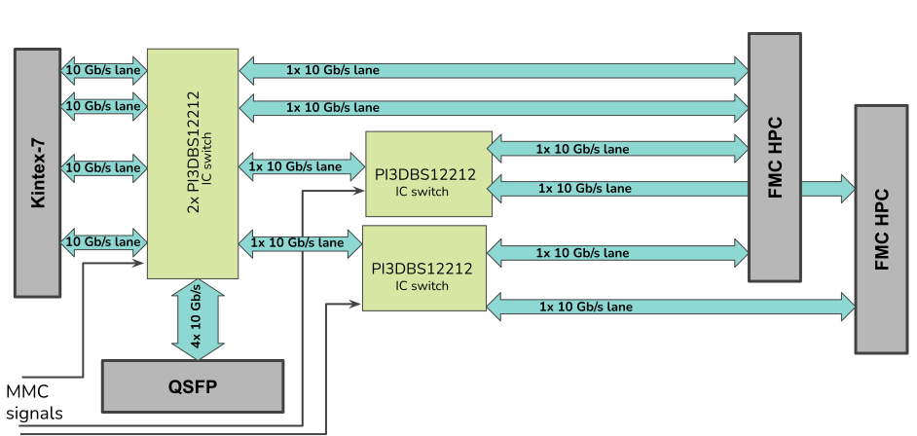
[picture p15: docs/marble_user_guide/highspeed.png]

 \caption{Transceivers routing block diagram.}\label{highspeed}
\end{center}
\end{figure}

\section{Clocking}
This section describes how and where clock signals are routed. There are 7 on-board clock sources:

\begin{table}[htbp]
\centering
\begin{tabular}{@{}llp{0.6\linewidth}@{}}
\toprule
Clock Name &
  Reference &
  Description \\ \midrule
\multirow{2}{*}{System Clock} &
  Y1, Y2 &
  Y1 and Y2 can be soldered interchangeably and provide a reference clock source for the U20 chip \\[0.1cm]
 &
  U20 &
 U20 is an ultra-low jitter clock generator that provides a 125 MHz clock for the FPGA bank 33 that can operate as a DDR3 reference clock. Additionally, U20 generates 125 MHz clock which is connected to the clock multiplexer.
   \\ [0.3cm]
Additional Clock &
  Y3 &
  VCXO - provides 20 MHz clock for FPGA bank 33 \\[0.2cm]
User Clock &
  Y6 &
  Si570 - provides variable clock frequencies for 10 MHz to 280 MHz; connected to the clock multiplexer \\[0.1cm]
\begin{tabular}[c]{@{}l@{}}User U.FL Clock 1\\ (differential pair)\end{tabular} &
  J2, J5 &
  External clock source input \\[0.4cm]
\begin{tabular}[c]{@{}l@{}}User U.FLClock 2\\ (differential pair)\end{tabular} &
  J3, J7 &
  External clock source input \\[0.4cm]
FMC1 M2C &
  P1 & GBTCLK 0 \& 1
   \\[0.5cm]
FMC2 M2C &
  P2 & GBTCLK 0 \& 1
   \\ \bottomrule
\end{tabular}
\caption{}
\label{tab:clk-table}
\end{table}

Marble supports external clock sources from FMC and from U.FL connectors. Thanks to the clock multiplexer, any clock input can be connected to any FPGA MGT clock input. Clock routing and Si570 frequency can be changed over I2C from the house-keeping microcontroller or the FPGA.

\begin{figure}[H]
\begin{center}
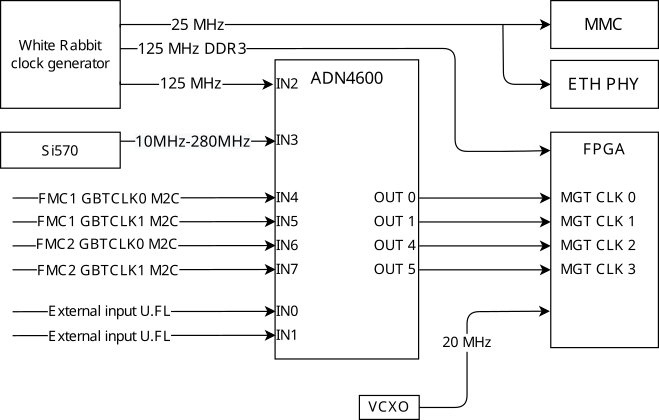
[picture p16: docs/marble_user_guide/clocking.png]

 \caption{Marble clocking scheme}\label{clocking}
\end{center}
\end{figure}

\subsection{White Rabbit clock generator}
The clock chips available on the board allow implementation of the White Rabbit protocol. White Rabbit provides sub-nanosecond accuracy and picoseconds precision of synchronization for large distributed systems.

\section{Pmod connectors}
Marble has 3 Pmod connectors that support 3.3V logic level:
\begin{enumerate}
	\item J12 and J13 are connected to FPGA
	\item J6 is connected the MMC
\end{enumerate}

\begin{table}[htbp]
\centering
\begin{tabular}{@{}cccc@{}}
\toprule
 &
  \begin{tabular}[c]{@{}c@{}}Pmod 1 (J12)\\ FPGA\end{tabular} &
  \begin{tabular}[c]{@{}c@{}}Pmod 2 (J13)\\ FPGA\end{tabular} &
  \begin{tabular}[c]{@{}c@{}}Pmod  (J16)\\ MMC\end{tabular} \\ \midrule
Pmodx\_C\_0 & IO\_L6N\_14 & IO\_L7P\_33 & PB9 (SEL)      \\
Pmodx\_C\_1 & IO\_L7N\_14 & IO\_L2N\_33 & PC3 (MOSI)     \\
Pmodx\_C\_2 & IO\_25\_14  & IO\_L4N\_33 & PC2 (MISO)     \\
Pmodx\_C\_3 & IO\_L7P\_14 & IO\_L7N\_33 & PB10 (SCK)     \\
Pmodx\_C\_4 & IO\_0\_14   & IO\_L2P\_33 & PB14 (EINT1)   \\
Pmodx\_C\_5 & IO\_L5N\_15 & IO\_L8P\_33 & PB15           \\
Pmodx\_C\_6 & IO\_L4P\_15 & IO\_L4P\_33 & PD6 (UART4 RX) \\
Pmodx\_C\_7 & IO\_L5P\_15 & IO\_L3N\_33 & PD5 (UART4 TX) \\ \bottomrule
\end{tabular}
\caption{Pmod connectors pins assignment}
\label{tab:pmod}
\end{table}

\begin{figure}[H]
\begin{center}
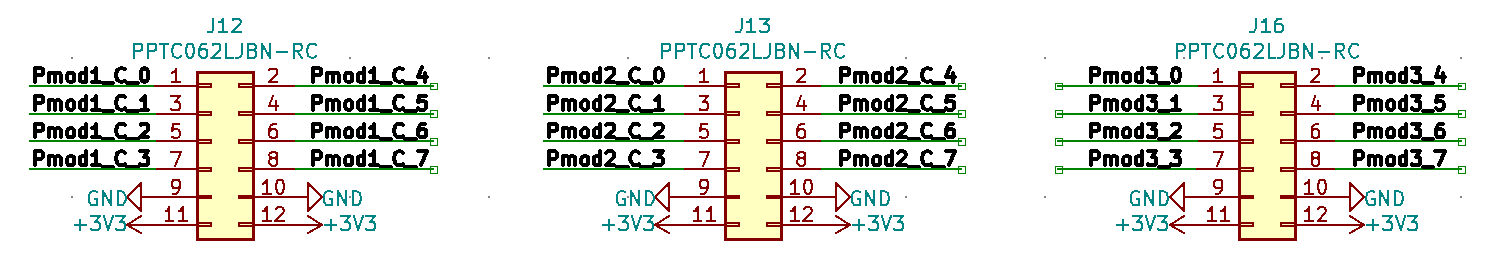
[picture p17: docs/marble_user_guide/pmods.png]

 \caption{Pmod pinout}\label{pmods}
\end{center}
\end{figure}

\section{QSFP}
Marble is equipped with 2 QSFP cages (\ref{qsfp}). Each can support 40 Gb/s of data transfer:
\begin{enumerate}
	\item QSFP number 1 - high-speed lines are directly connected to the FPGA bank 116
	\item QSFP number 2 - high-speed lines are connected to the FPGA bank 115 through the gigabit multiplexer.
\end{enumerate}

QSFPs control signals are connected to the I2C IO expander (U34)(\ref{qsfpio}) which is accessible from FPGA or MMC.
The connection of the differential signals to the FPGA is shown in the tables (\ref{tab:qsfp1-table})(\ref{tab:qsfp2-table}).
QSFP2 is not directly connected to the FPGA chip, but is instead connected via a gigabit multiplexer which is controlled from the MMC.
By default, the multiplexer is configured to connect the QSFP2 to the FPGA.
To select a different configuration or restore the default, select the appropriate option from the MMC console or use the MMC's mailbox interface (\ref{sec:MMC:Mailbox}).

\begin{figure}[H]
\begin{center}
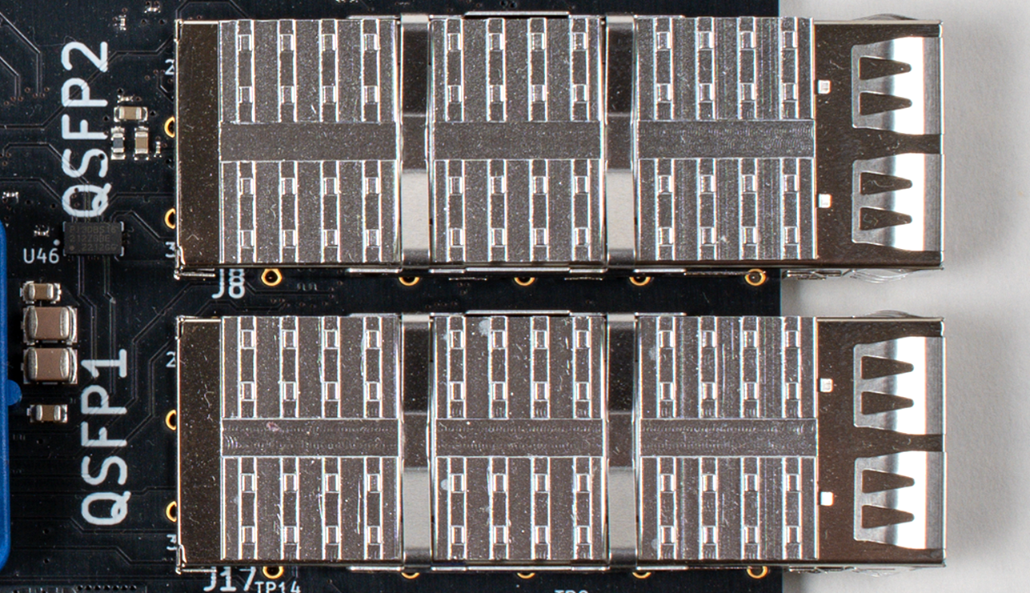
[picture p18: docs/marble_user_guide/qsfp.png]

 \caption{QSFP cages}\label{qsfp}
\end{center}
\end{figure}

\begin{figure}[H]
\begin{center}
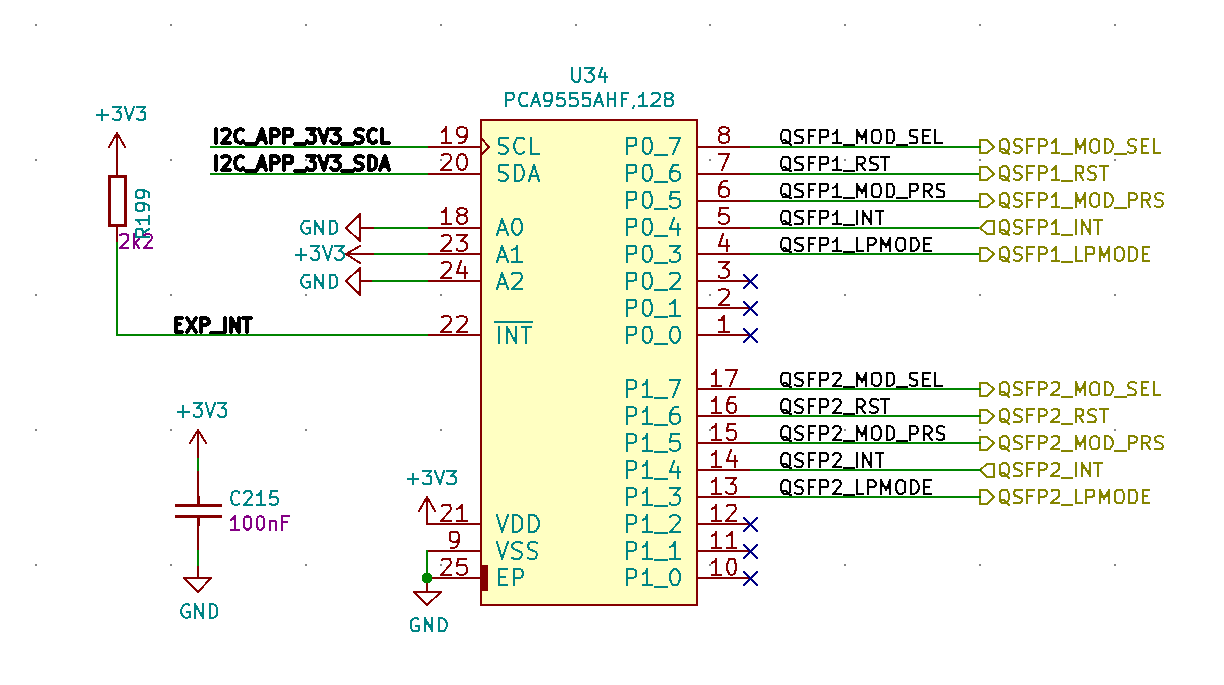
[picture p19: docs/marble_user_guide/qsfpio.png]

 \caption{I2C IO expander which controls QSFPs signals}\label{qsfpio}
\end{center}
\end{figure}

\begin{table}[htbp]
\centering
\begin{tabular}{@{}ll@{}}
\toprule
FPGA Pin     & QSFP Signal  \\ \midrule
MGTXTXP0\_116 & QSFP1\_TX\_3\_P \\
MGTXTXN0\_116 & QSFP1\_TX\_3\_N \\
MGTXRXP0\_116 & QSFP1\_RX\_3\_P \\
MGTXRXN0\_116 & QSFP1\_RX\_3\_N \\ \midrule
MGTXTXP1\_116 & QSFP1\_TX\_1\_P \\
MGTXTXN1\_116 & QSFP1\_TX\_1\_N \\
MGTXRXP1\_116 & QSFP1\_RX\_1\_P \\
MGTXRXN1\_116 & QSFP1\_RX\_1\_N \\ \midrule
MGTXTXP2\_116 & QSFP1\_TX\_2\_P \\
MGTXTXN2\_116 & QSFP1\_TX\_2\_N \\
MGTXRXP2\_116 & QSFP1\_RX\_2\_P \\
MGTXRXN2\_116 & QSFP1\_RX\_2\_N \\ \midrule
MGTXTXP3\_116 & QSFP1\_TX\_4\_P \\
MGTXTXN3\_116 & QSFP1\_TX\_4\_N \\
MGTXRXP3\_116 & QSFP1\_RX\_4\_P \\
MGTXRXN3\_116 & QSFP1\_RX\_4\_N \\ \bottomrule
\end{tabular}
\caption{QSFP1 pins connection}
\label{tab:qsfp1-table}
\end{table}

\begin{table}[htbp]
\centering
\begin{tabular}{@{}ll@{}}
\toprule
FPGA Pin     & QSFP Signal  \\ \midrule
MGTXTXP0\_115 & QSFP1\_TX\_3\_P \\
MGTXTXN0\_115 & QSFP1\_TX\_3\_N \\
MGTXRXP0\_115 & QSFP1\_RX\_3\_P \\
MGTXRXN0\_115 & QSFP1\_RX\_3\_N \\ \midrule
MGTXTXP1\_115 & QSFP1\_TX\_1\_P \\
MGTXTXN1\_115 & QSFP1\_TX\_1\_N \\
MGTXRXP1\_115 & QSFP1\_RX\_1\_P \\
MGTXRXN1\_115 & QSFP1\_RX\_1\_N \\ \midrule
MGTXTXP2\_115 & QSFP1\_TX\_2\_P \\
MGTXTXN2\_115 & QSFP1\_TX\_2\_N \\
MGTXRXP2\_115 & QSFP1\_RX\_2\_P \\
MGTXRXN2\_115 & QSFP1\_RX\_2\_N \\ \midrule
MGTXTXP3\_115 & QSFP1\_TX\_4\_P \\
MGTXTXN3\_115 & QSFP1\_TX\_4\_N \\
MGTXRXP3\_115 & QSFP1\_RX\_4\_P \\
MGTXRXN3\_115 & QSFP1\_RX\_4\_N \\ \bottomrule
\end{tabular}
\caption{QSFP2 pins connection}
\label{tab:qsfp2-table}
\end{table}

\section{Ethernet}
Marble is equipped with one Ethernet PHY chip (Marvell 88E1512) which supports\hfil\break
10/100/1000BASE-T
(Bedrock firmware only supports 1000BASE-T) and connects to a network via RJ45 connector \hbox{J4}.
It attaches to FPGA bank 16 via an RGMII interface:

\begin{table}[htbp]
\centering
\begin{tabular}{@{}cc@{}}
\toprule
\textbf{RGMII signal}              & \textbf{FPGA pin}                \\ \midrule
RGMII\_RXD0                        & IO\_L4N\_16                      \\
RGMII\_RXD1                        & IO\_0\_16                        \\
RGMII\_RXD2                        & IO\_L1P\_16                      \\
RGMII\_RXD3                        & IO\_L1N\_16                      \\
RGMII\_RX\_DV                      & IO\_L4P\_16                      \\
RGMII\_RX\_CLK                     & IO\_L14P\_16                     \\
RGMII\_TXD0                        & IO\_L6N\_16                      \\
RGMII\_TXD1                        & IO\_L6P\_16                      \\
RGMII\_TXD2                        & IO\_L8N\_16                      \\
RGMII\_TXD3                        & IO\_L8P\_16                      \\
RGMII\_TX\_EN                      & IO\_L10P\_16                     \\
\multicolumn{1}{l}{RGMII\_TX\_CLK} & \multicolumn{1}{l}{IO\_L11N\_16} \\
PHY\_RSTn                          & IO\_L10N\_16                     \\ \bottomrule
\end{tabular}
\caption{RGMII pins assignment}
\label{tab:rgmii}
\end{table}

The Ethernet PHY can be monitored over MDIO by the MMC. To read the internal PHY configuration registers, select the appropriate option from the MMC console.
% By default, the MDIO address is set to 1, but it can be changed by changing the resistor on the module. To set address to 0, desolder resistor R80 and solder resistor R65 with value 0R.
% Note that this would require commensurate customization of the MMC's firmware.

The IP and MAC addresses are stored in the MMC's internal EEPROM memory (EEPROM functionality is emulated in the internal flash).
After the FPGA boots, this information is passed to the FPGA over the pseudo-SPI mailbox (\ref{sec:MMC:Mailbox}).
This feature depends, of course, on having a bitfile that implements it; this is a standard part of Bedrock's test\_marble\_family bitfiles.

\section{FMC}
Both FMC sockets are equipped with HPC (High Pin Count) type connector but not all signals were connected to FPGA and MMC.
The connection of both FMC connectors is shown below:
\begin{enumerate}
    \item \textbf{FMC P1} signal connection:
    \begin{enumerate}
        \item LA00...LA33 - connected to FPGA banks 15 and 16.
        \item HA00...HA23 - \textit{not connected}.
        \item HB00...HB21 - \textit{not connected}.
        \item CLK[0..1]\_M2C - connected to FPGA bank 15.
        \item GBTCLK[0..1]\_M2C - connected to CLK MUX IN4 and IN5.
        \item DP[0]\_M2C - connected to high speed MUX.
        \item DP[0]\_C2M - connected to high speed MUX.
        \item JTAG - connected to MMC.
        \item I2C - connected to I2C bus shared with MMC and FPGA
    \end{enumerate}
    \item \textbf{FMC P2} signal connection:
    \begin{enumerate}
        \item LA00...LA33 - connected to FPGA banks 12 and 14.
        \item HA00...HA23 - connected to FPGA bank 13.
        \item HB00...HB21 - \textit{not connected}.
        \item CLK[0..1]\_M2C - connected to FPGA banks 12 and 14.
        \item GBTCLK[0..1]\_M2C - connected to CLK MUX IN6 and IN7.
        \item DP[0..3]\_M2C - connected to high speed MUX.
        \item DP[0..3]\_C2M - connected to high speed MUX.
        \item JTAG - connected to MMC.
        \item I2C - connected to I2C bus shared with MMC and FPGA
    \end{enumerate}
\end{enumerate}

\section{USB-UART}
The USB-UART bridge (FT4232H) has 2 channels of UART:
\subsection{FPGA UART}
FPGA UART occupies FT4232's channel 3. UART signals are connected to bank 15 pins:
\begin{enumerate}
	\item TX input IO\_L1P\_15
	\item RX output IO\_0\_15
\end{enumerate}
\subsection{MMC UART}
MMC UART occupies FT4232's channel 4 and is used as the MMC serial console. Terminal configuration is 1N8 115200 baudrate. The FT4232's channel 2 DTR signal can be used to provide a reset signal for the microcontroller.
See \ref{sec:MMC:Console} for details about the console interface.

\section{Power}
Several hardware options are available to provide the nominal +12V power to the board.
It can come from TE Connector (3-641119-2) - J19 (fig. \ref{j19}) or by standard barrel connector (Type A: 5.5 mm OD, 2.1 mm ID) - J1. Input voltage range: 6V - 15V. Additionally, PoE can be used to power the module.

\begin{figure}[H]
\begin{center}
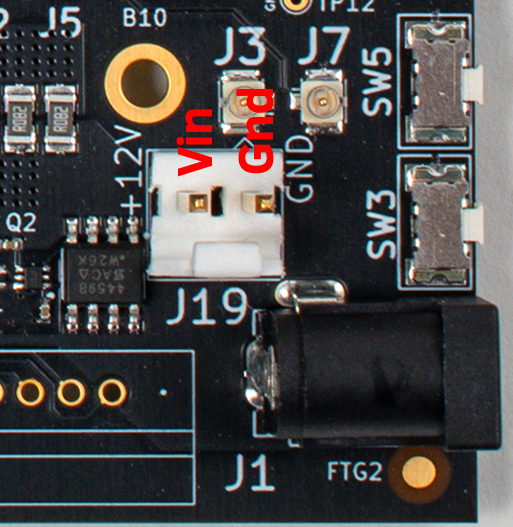
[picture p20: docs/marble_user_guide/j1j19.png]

 \caption{J19 connector with indicated Vin and GND}\label{j19}
\end{center}
\end{figure}

When the power is connected, the board starts up automatically. If there is a failure of any power rail, the LED corresponding to it will not light up.

Block diagram of Marble's power tree is shown in figure \ref{pwr}. The USB-UART bridge is powered from the micro USB connector via a converter (U22). The supervising microcontroller has a separate converter (U18) connected directly to the power input. The main voltages supplying the FPGA are produced by U35 - the programmable power management system. U35 turns on the individual power channels in the proper sequence and provides power to the additional converter (U58) and LDOs (U31, U36, U37, U47).

\begin{figure}[H]
\begin{center}
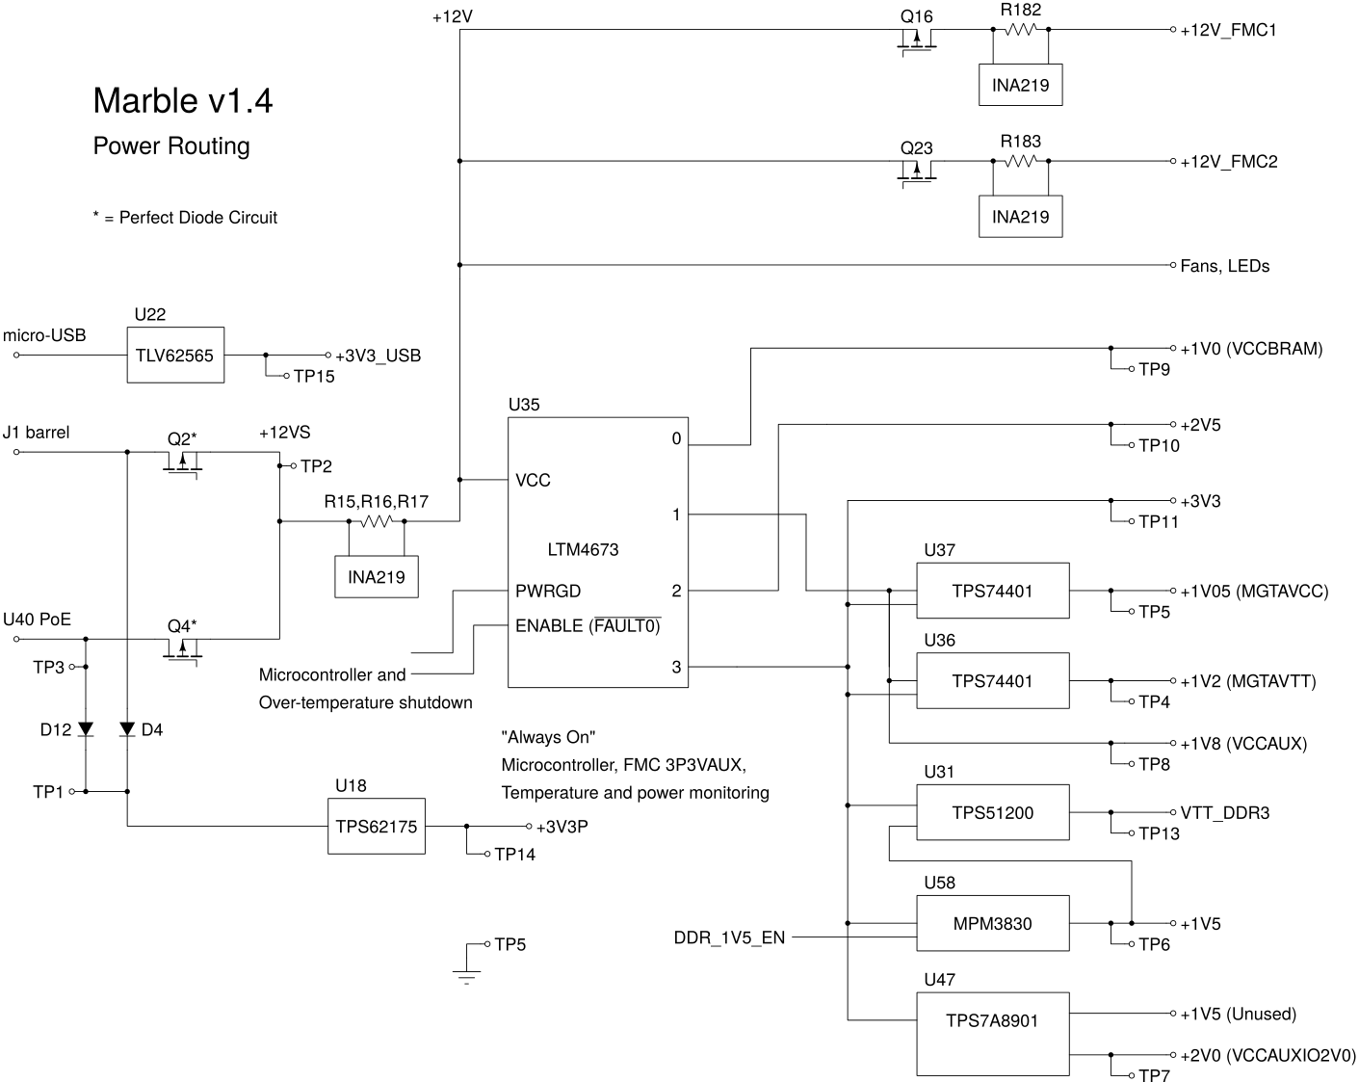
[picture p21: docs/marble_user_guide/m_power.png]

 \caption{Marble power routing}\label{pwr}
\end{center}
\end{figure}

Power supply features:
\begin{enumerate}
	\item Over-temperature protection.
	\item Power rails for the FPGA can be switched off and on by the microcontroller.
	\item All power rails generated by the LTM4673 can be monitored by the microcontroller and they are equipped with over-current protection.
	\item Current consumption, voltage and rails status can be read by microcontroller.
	\item The presence of the power rails is indicated by LED diodes
	\item 12V power supply for both FMCs can be controlled independently by the microcontroller. Additionally,  current can be measured.
\end{enumerate}
\subsection{Fan controller}
The fan control and temperature monitoring of the FPGA chip is done with the MAX6639 chip. Selection, mounting, and configuration of the fans is outside the scope of this document. The fans can be automatically controlled by measuring the temperature on the diode inside the FPGA. If the temperature exceeds a preset alarm threshold an ALERT signal will be issued. If the temperature continues to rise and exceeds another threshold, an "OVER-TEMP" signal will be issued and the FPGA will automatically power down. Through the I2C interface it is possible to read and write all MAX6639 configuration registers. Additionally, signals from both fan tachometers are monitored.

Two additional temperature sensors based on the LM75 chip provide temperature measurements around the main power converter and under the FMC P1 card. By default they are set to shut down the main power inverter when it exceeds 75 C.

\begin{figure}[H]
\begin{center}
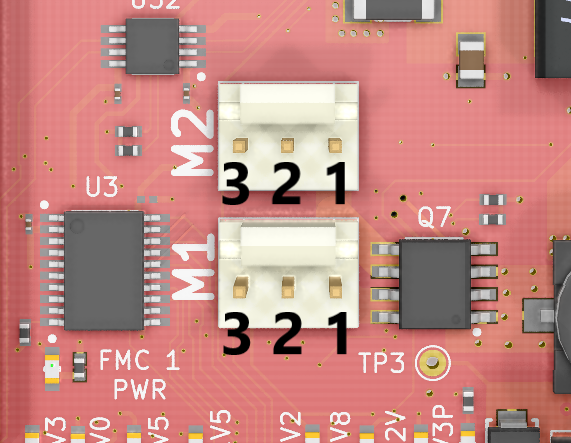
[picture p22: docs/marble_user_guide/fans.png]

 \caption{Fan connectors}\label{fans}
\end{center}
\end{figure}

\begin{table}[htbp]
\centering
\begin{tabular}{@{}llll@{}}
\toprule
\multicolumn{2}{c}{\textbf{M1}} & \multicolumn{2}{c}{\textbf{M2}} \\ \midrule
1            & GND              & 1            & GND              \\
2            & 12V              & 2            & 12V              \\
3            & Tacho            & 3            & Tacho            \\ \bottomrule
\end{tabular}
\caption{}
\label{tab:fan_connectors}
\end{table}

\section{MMC}\label{sec:MMC}
Module Management Controller (MMC) is based on STM32F207 microcontroller and provides housekeeping functions such as:
\begin{enumerate}
	\item Simple UART console over USB-UART bridge to control all functions
	\item Monitoring voltage, current consumption and warning signals on power rails
	\item Temperature monitoring at several locations
	\item Controlling and monitoring fans
	\item Configuring clock multiplexer
	\item Configuring MGT switches
	\item Resetting FPGA and controlling booting
	\item Programming Power Management Controller
	\item Controlling FMC power delivery and the presence of the cards
	\item Ensuring communication over MDIO with Ethernet PHY
	\item Ensuring communication over SPI with FPGA
\end{enumerate}

\subsection{Programming}\label{sec:MMC:Programming}
MMC programming can be done by using external tools such as STM Nucleo-SWD programmer, SEGGER J-Link Mini (Fig. \ref{mmcjtag}, Fig. \ref{mmcjtagswd}).

\begin{figure}[H]
\begin{center}
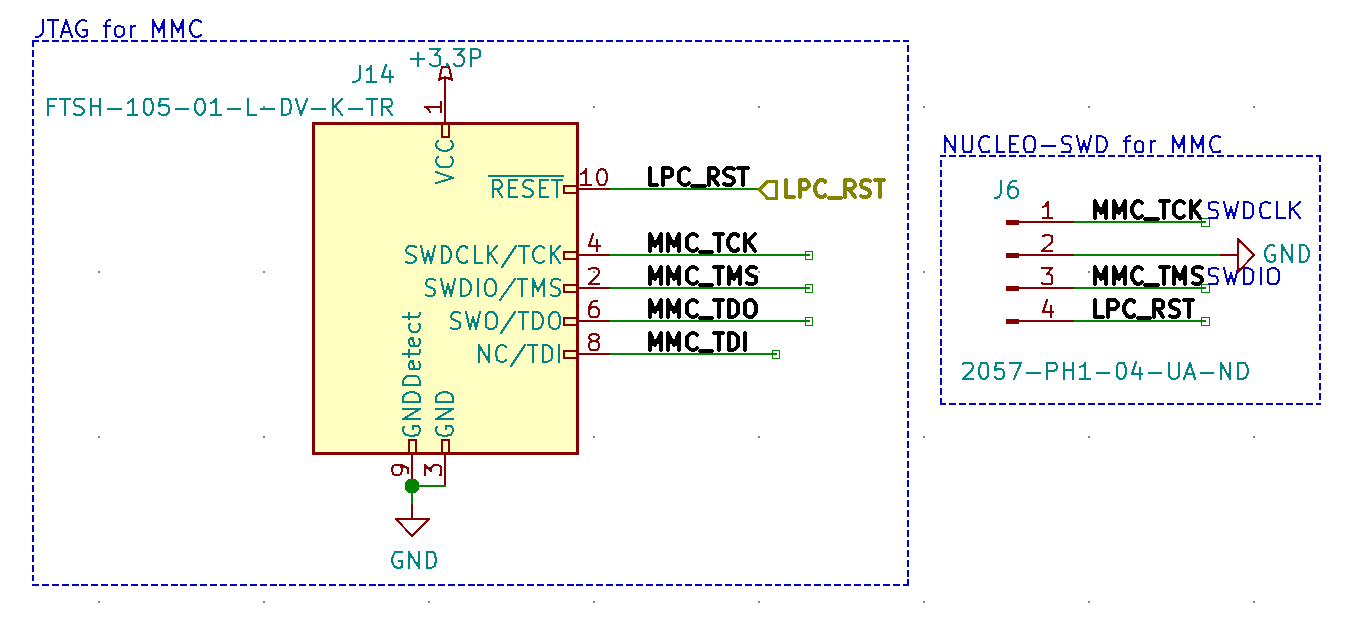
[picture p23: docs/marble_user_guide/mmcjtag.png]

 \caption{MMC JTAG and SWD interfaces}\label{mmcjtag}
\end{center}
\end{figure}

\begin{figure}[H]
\begin{center}
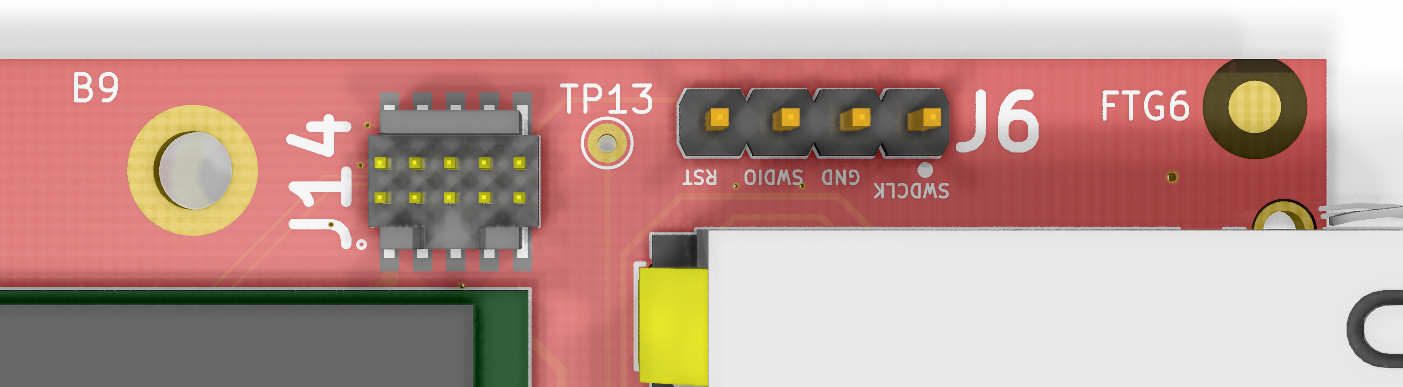
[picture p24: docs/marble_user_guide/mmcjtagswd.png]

 \caption{MMC JTAG and SWD connectors}\label{mmcjtagswd}
\end{center}
\end{figure}

Download the latest version of the microcontroller testing code from GitHub:
\begin{leftbar}
\url{https://github.com/BerkeleyLab/Marble-MMC}
\end{leftbar}

A recent version of OpenOCD (v0.10.0 or later) is required.
\begin{enumerate}
	\item Connect JTAG module to \textbf{J14}
	\item Connect the micro USB cable and using the serial terminal, connect to the last serial port for the new listed in the operating system. Use 115200 baudrate.
	\item Power up the board.
	\item Program the microcontroller using the following commands:
	\begin{enumerate}
	\item Go to the main folder of the downloaded repository.
	\item Open command terminal and run command:
	\begin{lstlisting}[backgroundcolor = \color{Gainsboro}, language=bash, frame=none]]
$ make marble_download
	\end{lstlisting}
	\end{enumerate}
	\item After successful programming, a menu in the serial terminal should appeared and LEDs (LD15, LD11, LD12) should blink in the "snake" pattern.
\end{enumerate}
\subsection{LEDs}
Three general purpose LEDs are connected to the MMC chip:
\begin{enumerate}
	\item LED11 - connected to pin PE1
	\item LED12 - connected to pin PE2
	\item LED15 - connected to pin PE0
\end{enumerate}

\subsection{Console}\label{sec:MMC:Console}
The MMC implements a console interface over its UART serial connection, intended primarily for human (as opposed to machine) interface.
The interface is line-based, meaning it processes text input after receiving a line-ending character, which can be one or both of
linefeed (ASCII/UTF-8 {\tt 0x0A}) or carriage return (ASCII/UTF-8 {\tt 0x0D}).
The terminal emulator (e.g. miniterm, minicom, etc) should append such a line ending to every message for proper processing the the MMC.
Note that this is \emph{not} the default behavior for many terminal emulators.
After opening the connection in a terminal emulator (115200 baudrate, 8N1), type a question mark ({\tt ?}) followed by a line ending to
view a summary of available options.

\subsection{I2C Tree}
Marble is equipped with two I2C buses (block diagram is shown in fig. \ref{i2c}):
\begin{enumerate}
	\item I2C\_PM - supports devices for power management, temperature measurement and fan control
	\item I2C\_FPGA - This bus is shared between the MMC and the FPGA chip. Through an I2C switch, it is connected to:
	\begin{enumerate}
		\item FMC 1 and FMC 2
		\item Clock multiplexer
		\item SO-DIMM module
		\item QSFP 1 and QSFP 2
		\item Current measurement devices, Si570 and IO expanders
	\end{enumerate}
\end{enumerate}
\begin{figure}[H]
\begin{center}
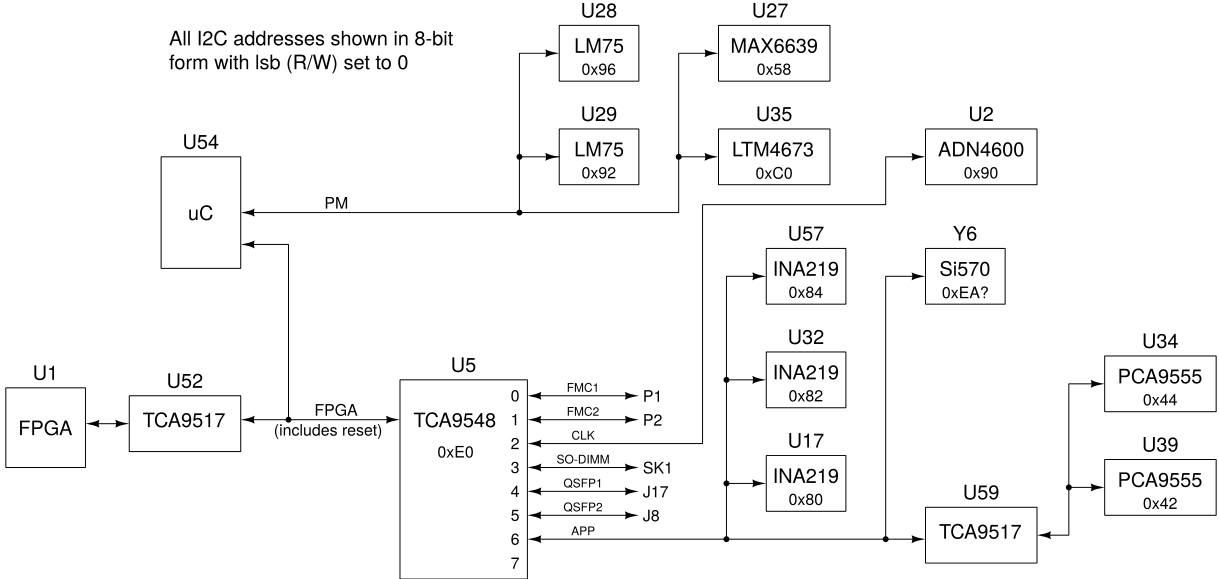
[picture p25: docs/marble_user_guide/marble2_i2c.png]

 \caption{I2C map}\label{i2c}
\end{center}
\end{figure}

\subsection{Pseudo-SPI Mailbox}\label{sec:MMC:Mailbox}
  The MMC can communicate with the FPGA via a dedicated SPI bus between the two ICs.
  The standard firmware image for Marble boards (at \url{https://github.com/BerkeleyLab/Marble-MMC}) implements a mailbox
  interface over this SPI bus which provides board information and configuration options to the FPGA application.
  For details, see that repo's {\tt doc/mailbox.md}.

\section{Mechanical dimensions}

\begin{figure}[H]
\begin{center}
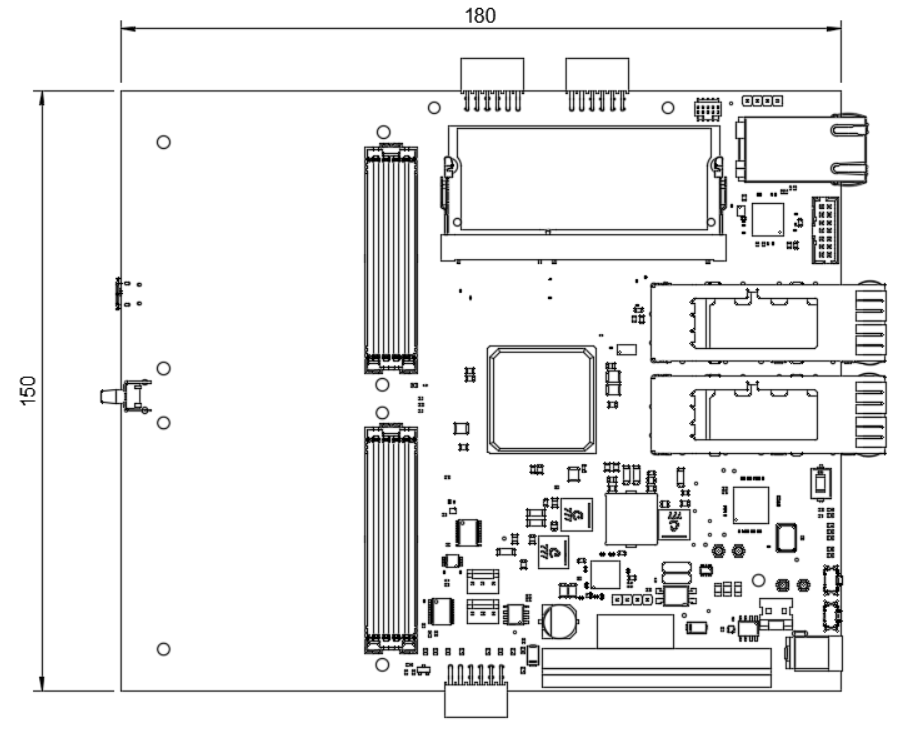
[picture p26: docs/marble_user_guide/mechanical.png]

 \caption{Mechanical dimensions}\label{mechanical}
\end{center}
\end{figure}

\begin{figure}[H]
\begin{center}
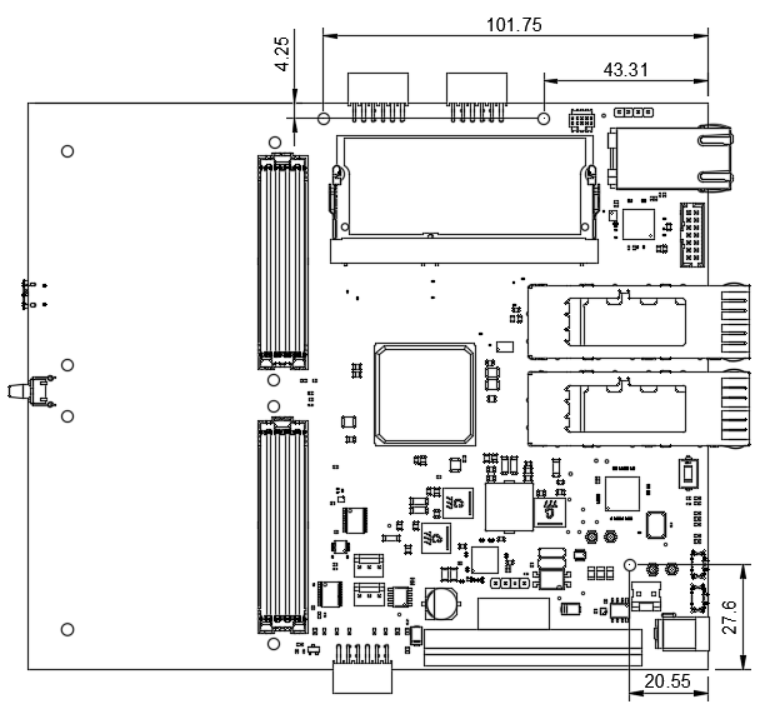
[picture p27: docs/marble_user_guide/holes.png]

 \caption{Mounting holes positioning}\label{holes}
\end{center}
\end{figure}

\begin{figure}[H]
\begin{center}
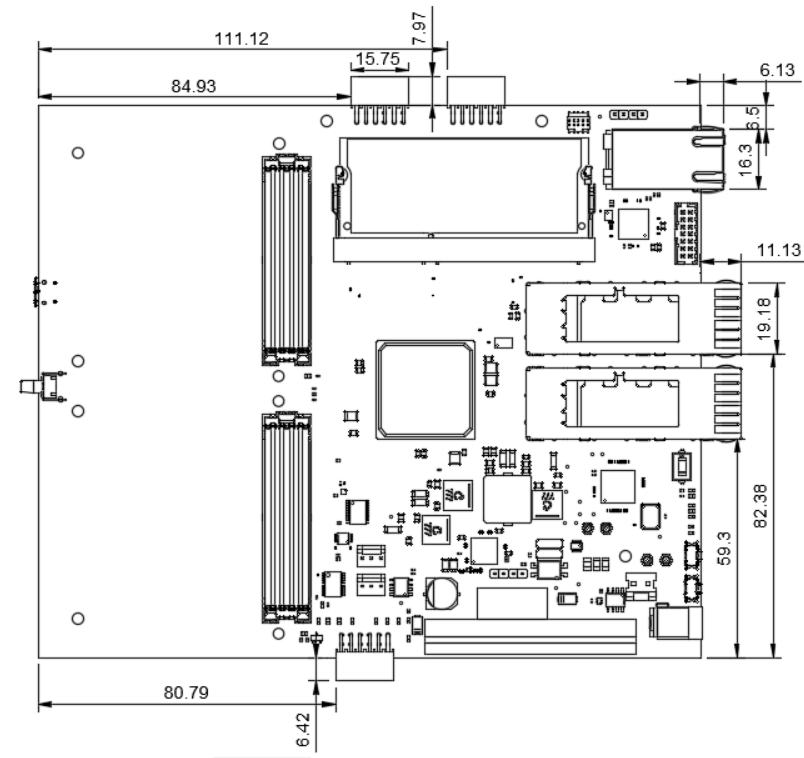
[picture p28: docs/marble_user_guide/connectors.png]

 \caption{Protruding connectors positioning}\label{connectors}
\end{center}
\end{figure}

\section{Appendix}
\subsection{Power supply test points}

\begin{figure}[H]
\begin{center}
% testpoint_map.pdf created with
%   gerbv -p testpoint_map.gvp -x pdf -o testpoint_map.pdf
% in the fab directory, after the fab package is made.

 \caption{Test point map}\label{testpoints}
\end{center}
\end{figure}

\begin{itemize}
	\item \textbf{TP1} - \textbf{input to +3.3P regulator}
	\item \textbf{TP2} - \textbf{+12VS}
	\item \textbf{TP3} - \textbf{PoE}
	\item \textbf{TP4} - \textbf{MGTAVTT (+1.2V)}
	\item \textbf{TP5} - \textbf{MGTAVCC (+1.05V)}
	\item \textbf{TP6} - \textbf{+1V5}
	\item \textbf{TP7} - \textbf{VCCAUXIO2V0 (+2.0V)}
	\item \textbf{TP8} - \textbf{VCCAUX (+1.8V)}
	\item \textbf{TP9} - \textbf{VCCBRAM (+1.0V)}
	\item \textbf{TP10} - \textbf{+2V5}
	\item \textbf{TP11} - \textbf{+3V3}
	\item \textbf{TP12} - \textbf{GND}
	\item \textbf{TP13} - \textbf{VTT\_DDR3 (+0.75V)}
	\item \textbf{TP14} - \textbf{+3.3P (always-on)}
	\item \textbf{TP15} - \textbf{+3V3\_USB}
% no vias, meaning they don't show up like the rest
% TP17  TSENSE3+
% TP18  TSENSE2
% TP19  TSENSE1

\end{itemize}

Test points 12-15 are not present on Marble v1.0.

\begin{thebibliography}{99}
\end{thebibliography}
\end{document}

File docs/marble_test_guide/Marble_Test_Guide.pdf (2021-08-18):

# Marble – Factory Acceptance Tests

v1.0 2020

### August 18, 2021

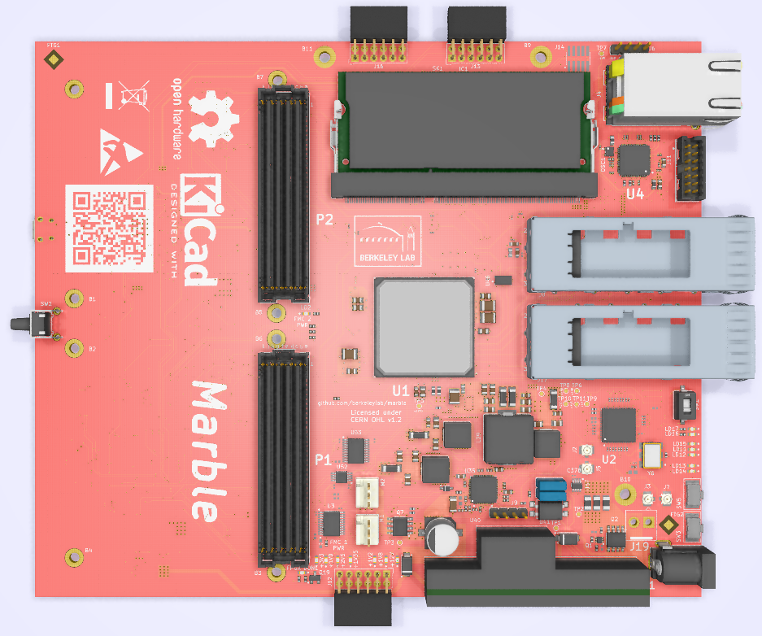
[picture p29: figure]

Introduction

This document presents a user–friendly guide on how to perform Factory Acceptance Tests (FAT) for the Marble module. Tests begin from a short description of where Marble’s useful connector, LED indicators, and test points are placed on the board. It is highly recommended to perform the tests in the order presented in this document.

## Contents

1 Overview | 3
1.1 Hardware requirements | | 3
1.2 Software requirements | | 3
2 Power connection | 3
3 Microcontroller programing | 5
4 Power Supply programing | 5
5 FPGA programing | 7
5.1 FMC test | | 7
5.2 QSFP test | | 9
5.3 Ethernet test | | 9
6 Appendix | 10
6.1 An alternative way to program FPGA | 10

## 1 Overview

Design les are open source and can be downloaded from GitHub: https://github.com/BerkeleyLab/Marble

Each board is marked with a revision number. Make sure that the downloaded les correspond to your board.

### 1.1 Hardware requirements

To perform all tests the following hardware is required:

1. Lab bench-top power supply.
2. Micro USB cable.
3. QSFP loopback module.
4. FMC Tester module.
5. Multimeter.
6. MMC JTAG (example: SEGGER J-LINK mini).
7. FPGA JTAG (example: Digilent JTAG HS3).

### 1.2 Software requirements

To perform all tests the following software is required:

1. Vivado 19.1.
2. Serial port terminal. Example Miniterm, can be installed by:

$ sudo apt - get install python3 - serial

## 2 Power connection

Before connecting the power supply for the first time, check that the main bus is not shorted. Using a multimeter set in resistance measurement mode, measure the resistance between metal pads of the J19 connector (Figure 1).

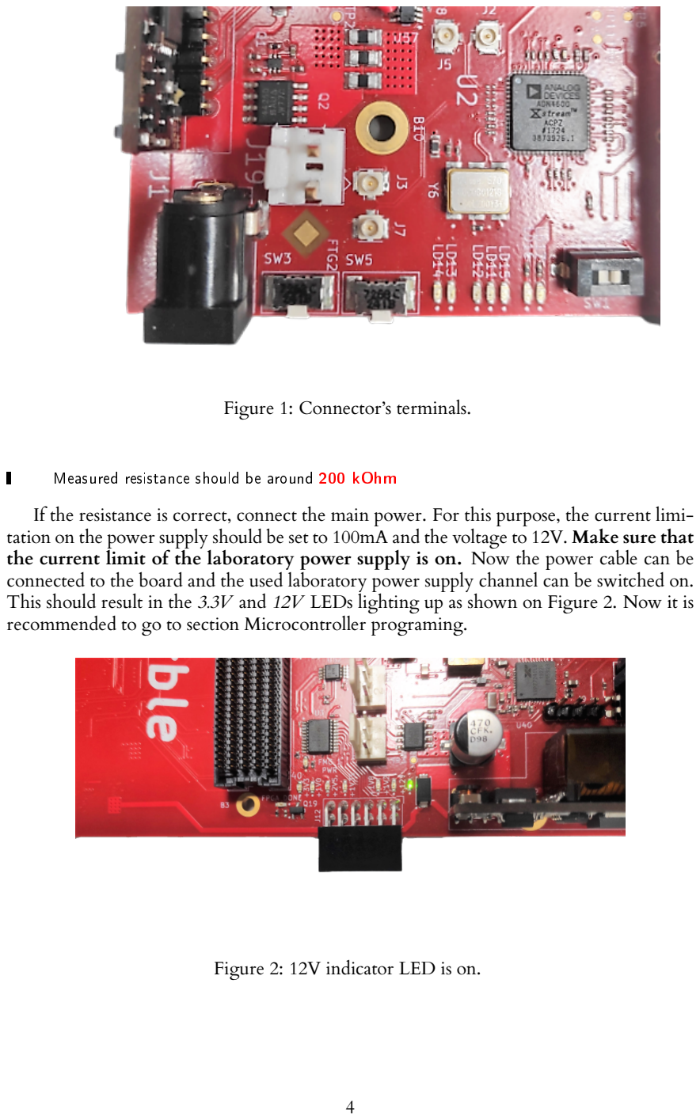
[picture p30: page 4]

Figure 1: Connector’s terminals.

Measured resistance should be around 200 kOhm
If the resistance is correct, connect the main power. For this purpose, the current limi-tation on the power supply should be set to 100mA and the voltage to 12V. Make sure that the current limit of the laboratory power supply is on. Now the power cable can be connected to the board and the used laboratory power supply channel can be switched on. This should result in the 3.3V and 12V LEDs lighting up as shown on Figure 2. Now it is recommended to go to section Microcontroller programing.

Figure 2: 12V indicator LED is on.

## 3 Microcontroller programing

Download the latest version of the microcontroller testing code from GitHub:

https://gitlab.lbl.gov/spaiagua/marble_mmc/-/tree/unied_marble

A recent version of OpenOCD (v0.10.0 or later) is required.
1. Connect JTAG module to J14 as shown on Figure 3.
2. Connect the micro USB cable and using the serial terminal, connect to the last serial port for the new listed device in the operating system. Use 115200 baudrate.
3. Power up the board.
4. Program the microcontroller using the following commands:
(a) Go to the main folder of the downloaded repository.
(b) From the command line, run the following:

$ make marble_download

5. After successful programming, a menu in the serial terminal should appear and LEDs (LD15, LD11, LD12) should blink.

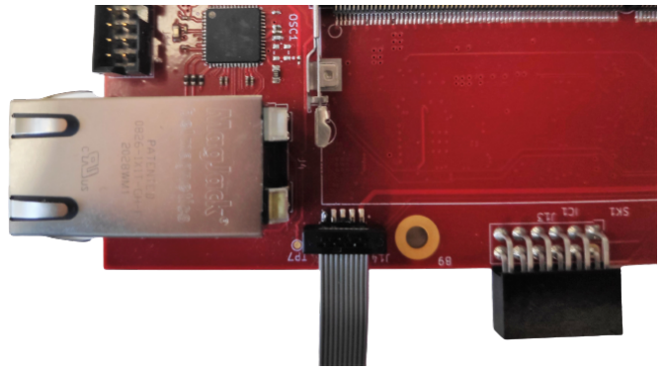
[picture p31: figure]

Figure 3: J14 connector.

## 4 Power Supply programing

Before doing the steps below it is highly recommended to verify that there are no shorts on the power rails. This can be done by measuring the resistance between the test points:

1. TP12 (GND) and TP7 (+2V0).
2. TP12 (GND) and TP9 (+1V0).

3. TP12 (GND) and TP10 (+2V5).
4. TP12 (GND) and TP8 (+1V8).
5. TP12 (GND) and TP6 (+1V5).
6. TP12 (GND) and TP4 (+1V2).
7. TP12 (GND) and TP11 (+3V3).
8. TP12 (GND) and TP15 (+3V3USB).
9. TP12 (GND) and TP14 (+3V3P).
10. TP12 (GND) and TP5 (+1V05).

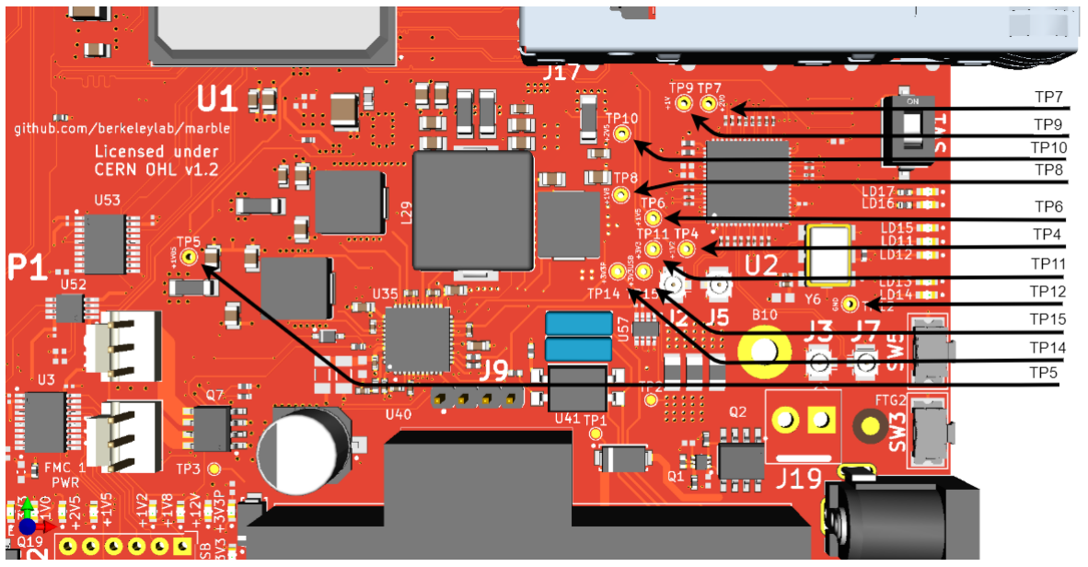
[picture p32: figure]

Figure 4: Test points.

Warning: Only perform the following steps if there are no shorts on the power rails.

1. Connect the micro USB cable and, using the serial terminal, connect to the last serial port for the new device listed in the operating system. Use 115200 baudrate.
2. Set up voltage to 12V and the current limit to 1A on a lab power supply.
3. Power up the board.
4. From the menu displayed in the serial terminal, select the option g) XRP7724 go .
5. Power cycle by turning the lab power supply Off and then On.
6. All power LED indicators should be On (Figure 5).
7. Using multimeter measure the voltage between the test points:

(a) TP12 (GND) and TP7 (+2V0) - expected voltage: +2.0V.
(b) TP12 (GND) and TP9 (+1V0) - expected voltage: +1.0V.
(c) TP12 (GND) and TP10 (+2V5) - expected voltage: +2.5V.
(d) TP12 (GND) and TP8 (+1V8) - expected voltage: +1.8V.
(e) TP12 (GND) and TP6 (+1V5) - expected voltage: +1.5V.
(f ) TP12 (GND) and TP4 (+1V2) - expected voltage: +1.2V.
(g) TP12 (GND) and TP11 (+3V3) - expected voltage: +3.3V.
(h) TP12 (GND) and TP15 (+3V3USB) - expected voltage: +3.3V.
(i) TP12 (GND) and TP14 (+3V3P) - expected voltage: +3.3V.
(j) TP12 (GND) and TP5 (+1V05) - expected voltage: +1.05V.

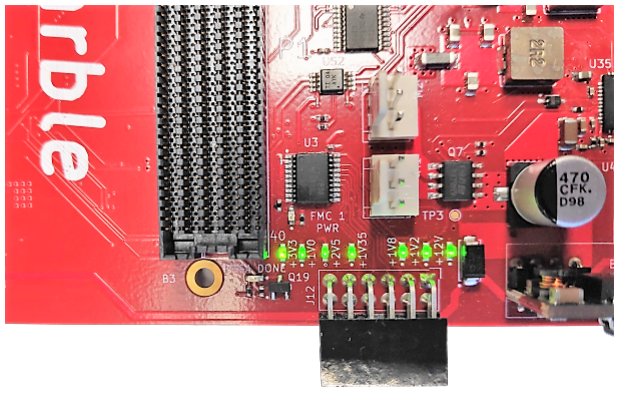
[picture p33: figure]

Figure 5: Power LED indicators after a successful power cycle.

## 5 FPGA programing

Download the latest version of the FPGA testing code from GitHub:

https://github.com/BerkeleyLab/Bedrock/

Before testing the FPGA it is recommended to set up the current limit to 2A on the lab power supply.

### 5.1 FMC test

Board power should be turned o when inserting and removing the FMC module.

1. Plug FMC Tester module to one of the FMC connectors as shown on Figure ??.

2. Connect the micro USB cable and, using the serial terminal, connect to the last serial port for the new device listed in the operating system. Use 115200 baudrate.
3. Change the network adapter settings to connect with static IP address 192.168.9.10.
4. Connect Marble to the computer using an Ethernet cable.
5. Power up the board.
6. In the serial terminal menu choose 4) GPIO control a) FMC power to turn on power to the FMCs.
7. Program the FPGA using the following steps:
(a) Go to the folder Bedrock/projects/test_marble_family/
(b) Open command terminal and run command:

$ mutil usb

8. To run a test do the following steps:
(a) Go to the folder Bedrock/projects/test_marble_family/
(b) To test P1 FMC connector run the following command:

$ PYTHONPATH =../../ badger :../../ periphera \ l_drivers / i2cbridge python fmc \ _test \ _c . py -- ip $IP -- fmc 0
(c) To test P2 FMC connector run the following command:

$ PYTHONPATH =../../ badger :../../ periphera \ l_drivers / i2cbridge python fmc \ _test \ _c . py -- ip $IP -- fmc 1

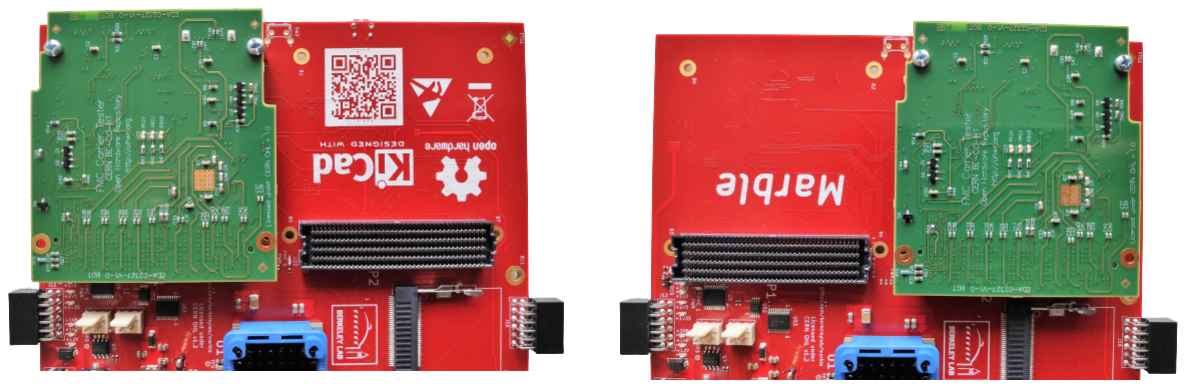
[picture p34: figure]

Figure 6: FMC connectors FMC Tester board plugged in.

### 5.2 QSFP test

Board power should be turned o when inserting and removing the QSFP module.

1. Plug QSFP loopback module to one of the ports.
2. Connect FPGA JTAG programmer.
3. Configure FPGA using marble_ibert.bit bit file.
(a) Run Vivado
(b) Go to Flow | Open Hardware Manager and then Tools | Auto Connect
(c) Click Tools | Program Device | xc7k160t_0 to open the programming window.
(d) Choose the bitstream file and click Program
4. After successful programming, the Dashboard should start automatically.
5. Detect links by clicking Serial I/O Links Auto-detect links
6. Correctly detected and working links should appear as shown in figure 7.
7. Connect the QSFP loopback module to the other QSFP connector and repeat the steps above.

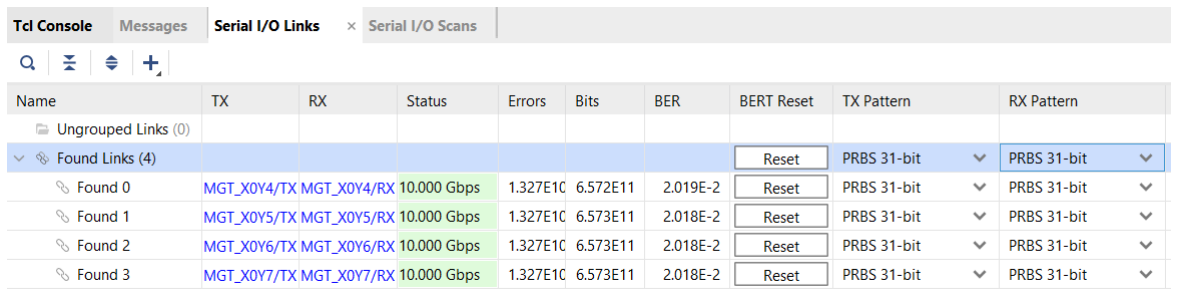
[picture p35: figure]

Figure 7: Working links.

### 5.3 Ethernet test

The following steps should be performed to test the Ethernet:

1. Program the FPGA using the following steps:
(a) Go to the folder Bedrock/projects/test_marble_family/
(b) Open command terminal and run command:

$ mutil usb

2. Change the network adapter settings to connect with static IP address 192.168.9.10.
3. Connect Marble to the computer using an Ethernet cable.

4. Ping the board:

$ ping 192.168.9.10

5. Expected result:

Pinging [192.168.9.10] with 32 bytes of data : Reply from 192.168.9.10: bytes =32 time =17 ms TTL =55 Reply from 192.168.9.10: bytes =32 time =152 ms TTL =55 Reply from 192.168.9.10: bytes =32 time =12 ms TTL =55 Reply from 192.168.9.10: bytes =32 time =14 ms TTL =55

Ping statistics for 192.168.9.10:
Packets : Sent = 4 , Received = 4 , Lost = 0 (0% loss ) , Approximate round trip times in milli - seconds :
Minimum = 12 ms , Maximum = 152 ms , Average = 48 ms
6. For data traffic test use iperf. Run command:

$ iperf -c 192.168.9.10 -u -b 1000 M -p 802

## 6 Appendix

### 6.1 An alternative way to program FPGA

Programming FPGA using Vivado and Digilent JTAG HS3:

1. Run Vivado
2. Go to Flow | Open Hardware Manager and then Tools | Auto Connect
3. Click Tools | Program Device | xc7k160t_0 to open the programming window.
4. Choose the bitstream file and click Program
5. After successful programming, the Dashboard should start automatically.

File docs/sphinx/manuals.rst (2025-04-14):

.. _general-docs:

Manuals
=======

For the Marble User Guide. See :download:`Marble User Guide<Marble_User_Guide.pdf>`

For the Marble Test Guide. See :download:`Marble Test Guide<Marble_Test_Guide.pdf>`

For the Marble Schematic. See :download:`Marble Schematic<Marble_Schematic.pdf>`

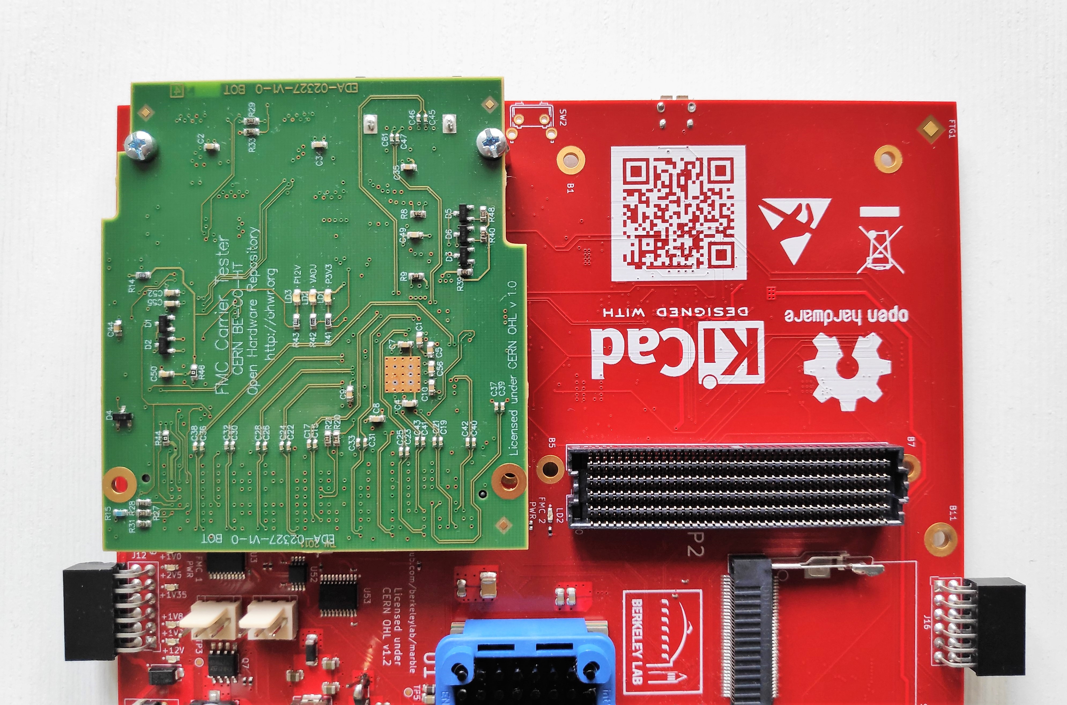
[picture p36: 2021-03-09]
docs/marble_test_guide/fmc1.jpg

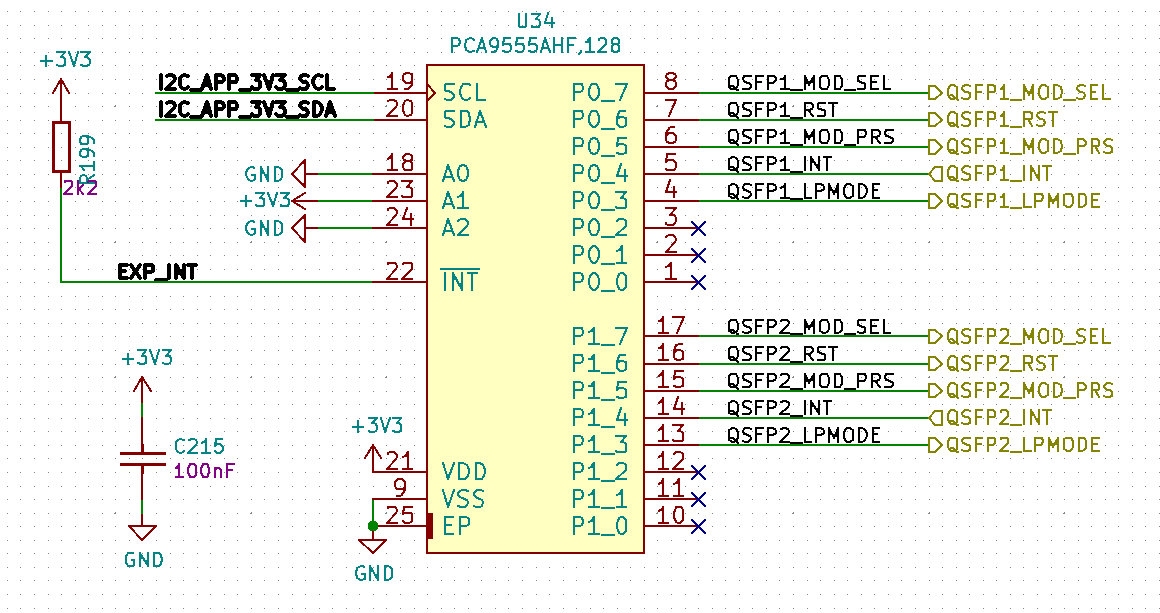
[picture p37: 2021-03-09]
docs/marble_user_guide/QSFPctrl.png

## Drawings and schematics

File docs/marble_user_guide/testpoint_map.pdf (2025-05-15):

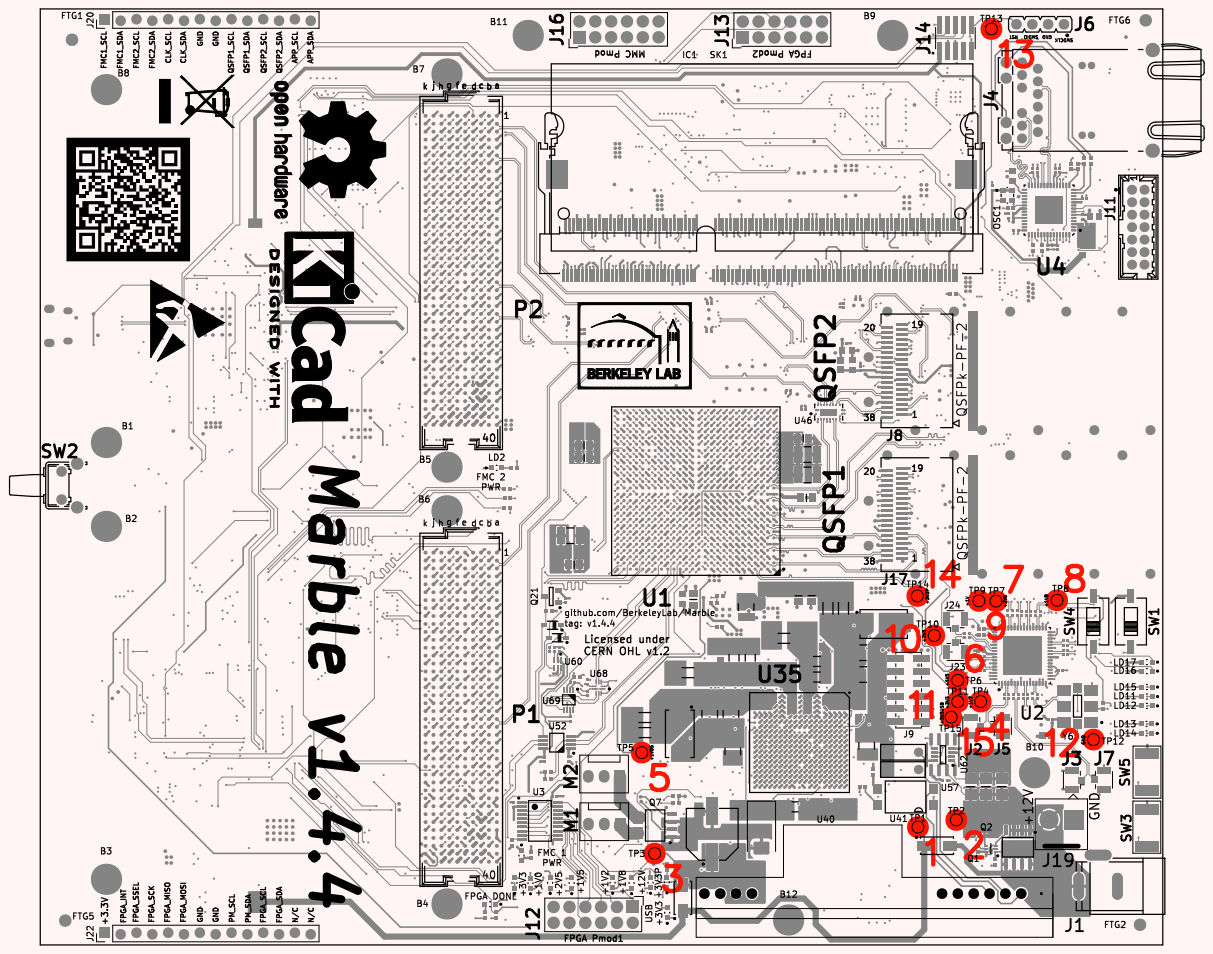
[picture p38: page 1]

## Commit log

2019-12-06 board name -> Marble Mini
    [MMC.sch]
2019-12-11 readme edited
    [FPGA_33_34.sch]
2019-12-16 MGT mux and QSFP added to the schematics,
    [AMC_FMC_Carrier-PcbDoc.sch, AMC_connector.sch, ETH_PHY.sch, FMC_1.sch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]
2020-01-02 FMC HPC & LPC done, FPGA power delivery done, RGMII lines done, MGT lines progress
    [AMC_FMC_Carrier-PcbDoc.sch, ETH_PHY.sch, FMC_1.sch, FMC_2.sch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]
2020-01-07 pcb progress
    [AMC_FMC_Carrier-PcbDoc.sch, FPGA.sch, FPGA_32_16.sch, I2C_MUX.sch]
2020-01-09 FPGA power finished, significant progress on PCB
    [AMC_FMC_Carrier-PcbDoc.sch, AMC_connector.sch, ETH_PHY.sch, FMC_1.sch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]
2020-05-20 new board outline, rearranging banks connections, SODIMM memory
    [AMC_FMC_Carrier-PcbDoc.sch, AMC_connector.sch, ETH_PHY.sch, FMC_1.sch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]
2020-05-22 DDR fanout done
    [AMC_FMC_Carrier-PcbDoc.sch, ETH_PHY.sch, FPGA.sch, FPGA_33_34.sch]
2020-05-26 FMC1 fanout and routing
    [AMC_FMC_Carrier-PcbDoc.sch, ETH_PHY.sch, FPGA.sch, FPGA_14_15.sch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]
2020-05-28 FMC1 routing done, FMC2 fanout
    [FPGA_12_13.sch, FPGA_14_15.sch, FPGA_32_16.sch, FPGA_PWR&MISC.sch]
2020-06-02 FMC2 routing done
    [FPGA.sch, FPGA_12_13.sch, FPGA_14_15.sch, FPGA_33_34.sch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]
2020-06-04 routing progress
    [AMC_FMC_Carrier-PcbDoc.sch, ETH_PHY.sch, FMC_1.sch, FMC_2.sch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]
2020-06-09 escape routing done
    [FPGA.sch, FPGA_12_13.sch, FPGA_14_15.sch, FPGA_32_16.sch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]
2020-06-12 MMC routing done
    [FPGA_12_13.sch, I2C_MUX.sch, MGT_CLK_Crosspoint.sch, MMC.sch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]
2020-06-16 clk switch power supply and general routing
    [FPGA_12_13.sch, FPGA_14_15.sch, FPGA_32_16.sch, FPGA_33_34.sch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]
2020-06-19 routing done
    [AMC_FMC_Carrier-PcbDoc.sch, FMC_1.sch, FMC_2.sch, FPGA_12_13.sch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]
2020-06-22 DDR lenght mached, 2 additional LEDs added, I2C pullups voltage changed and other minor changes
    [AMC_FMC_Carrier-PcbDoc.sch, FMC_1.sch, FMC_2.sch, FPGA.sch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]
2020-06-25 testpoints added, LEDs on the right site and other minor changes
    [FMC_1.sch, FMC_2.sch, FPGA.sch, FPGA_14_15.sch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]
2020-06-26 silks edited, diff pairs skew mached
    [FMC_1.sch, FMC_2.sch, Power.sch, Power_SW.sch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]
2020-07-14 REF CLK for MIG
    [AMC_FMC_Carrier-PcbDoc.sch, FPGA.sch, FPGA_33_34.sch, FPGA_MGT.sch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]
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2020-10-07 fixed bugs
    [ETH_PHY.sch, FMC_1.sch, FMC_2.sch, FPGA_14_15.sch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]
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2020-10-12 16 warnings, 16 errors
    [ETH_PHY.sch, FMC_1.sch, FMC_2.sch, FPGA.sch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]
2020-10-14 shave ERC report down to 5 issues
    * mostly by adding power inputs / outputs to the symbols (many
    power pins were set to bidirectional, which causes issues)
    * remove some stray power symbols which were not connected to
    anything
    * FMC connector: change all VCC and GND pins to Power input type
    (there's a lot of them!!)
    [FPGA_PWR&MISC.sch, MMC.sch, Marble.sch, Power.sch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]
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2020-11-18 fixed a corrupted schematic
    [Power_SW.sch, WhiteRabbit.sch]
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2020-11-18 fixed drc errors, removed Q25, more test points
    [Power.sch, SDRAM.sch, USB.sch]
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2020-11-19 U42 bug fixed, less DRC errors
    [FPGA_33_34.sch]
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2020-11-26 Adjust BOM details
    Fix spelling of "config" attribute for SW2
    Part number changes:
    FC68148 (DC-10A) to FC68148
    TXB0108PW to TXB0108PWR
    XRP7724ILBTR-F to XRP7724ILB-F
    [FPGA_14_15.sch, FPGA_33_34.sch, MMC.sch, PMOD.sch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]
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2020-11-28 Very minor clean-up
    Remove backup file kicad_libs/Pads.bck
    Add *.bck to .gitignore
    Fix spelling of Bidirectional, Programmable
    [ETH_PHY.sch, Power_SW.sch]
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2020-11-29 Use consistent and correct description for PLATED_HOLE3.0_PAD5.0
    Plated Through Hole: Hole Dia.=3.0mm Pad Dia.=5.0mm
    Cuts lint count by 24
    [Marble.sch]
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2020-12-10 fixed bug with MDIO level transkator, PHY address changed to 1
    [ETH_PHY.sch, FMC_1.sch, FMC_2.sch, FPGA.sch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]
2020-12-12 marble2_i2c.eps: fix typo
    FMC1 is P1, not J6
    Update image in I2C_MUX.sch, following instructions in scripts/README.md
    [I2C_MUX.sch]
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2021-01-13 Subtle changes to part numbers in database
    Improve alignment between schematic and libs
    Correct some part numbers and manufacturer names
    Parts affected:
    MARVELL 88E1512-A0-NNP2I000
    TAITIEN TXEAADSANF-25.000000
    INFINEON BAT165AX
    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
    [ETH_PHY.sch, Power.sch, USB.sch]
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2021-02-15 fixed issue with FPGA booting by adding POWER GOOD signal to keep FPGA in reset during power on; U36 and U37 BIAS connected to 3V3P; added other transistor to reset clock mux during power on
    [FPGA.sch, FPGA_PWR&MISC.sch, MMC.sch, Marble.sch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]
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2021-07-28 Fix value field for 22K resistors
    No longer described as 2.2K, 16 places
    BOM error caught by fab house
    Update attrib_lint.py to detect this fault
    [I2C_MUX.sch]
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2022-01-21 repo fixed, added new LDO for AUXIO2V0, new DCDC converter (U18) for 3V3P
    [ETH_PHY.sch, FMC_1.sch, FMC_2.sch, FPGA.sch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]
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2022-02-21 buffering, solved ERC issues
    [FPGA.sch, FPGA_MGT.sch, GBX_MUX.sch, Marble.sch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]
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2022-06-29 fixed issues with: 1V5 rail, FMC pins, I2C pull-up resistors
    [FMC_1.sch, FMC_2.sch, I2C_MUX.sch, JTAG.sch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]
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2022-08-24 I2C_MUX.sch: fix metadata of 2K2 resistors
    Make sure they land in BOM as actually 2K2, same line item as existing 2K2
    [I2C_MUX.sch]
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2023-02-26 Moved project to KiCad 6; reduced DRC errors to a few
    Moved project to KiCad 6; reduced DRC errors to a few
    [ETH_PHY.kicad_sch, FMC_1.kicad_sch, FMC_2.kicad_sch, FPGA.kicad_sch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]
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2023-02-28 fixed parts numners
    [FMC_1.kicad_sch, FMC_2.kicad_sch, LTM4673.kicad_sch, Marble.kicad_sch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]
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2023-03-19 Fixed part numbers for C127 and D10
    Fixed part numbers for C127 and D10
    [FMC_2.kicad_sch, FPGA_PWR&MISC.kicad_sch, LTM4673.kicad_sch, Marble.kicad_sch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]
2023-03-20 no ERC issues
    no ERC issues
    [FMC_2.kicad_sch, FPGA_14_15.kicad_sch, GBX_MUX.kicad_sch, LTM4673.kicad_sch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]
2023-03-21 Restore some consistency in schematic metadata
    Still 13 problematic footprint names in LTM4673.kicad_sch:
    BAD Dup: "Footprint" "CAPC1608X87N" "Capacitors SMD:CAPC1005X55N" in LTM4673-altium-import:0_Capacitor - non polarized
    BAD Dup: "Footprint" "CAPC2012X135N" "CAPC1608X87N" in LTM4673-altium-import:1_Capacitor - non polarized
    BAD Dup: "Footprint" "CAPC1608X87N" "Capacitors SMD:CAPC1005X55N" in LTM4673-altium-import:1_Capacitor - non polarized
    BAD Dup: "Footprint" "CAPC3216X180N" "CAPC3225X270N" in LTM4673-altium-import:1_Capacitor - non polarized
    BAD Dup: "Footprint" "CAPC1608X87N" "Capacitors SMD:CAPC1005X55N" in LTM4673-altium-import:0_Capacitor - non polarized
    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
    [ETH_PHY.kicad_sch, FMC_1.kicad_sch, FMC_2.kicad_sch, FPGA_14_15.kicad_sch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]
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2023-03-30 Fix duplicate parts in BOM and add missingpart numbers to some
    [LTM4673.kicad_sch, Marble.kicad_sch]
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2023-04-16 routing done, no DRC errors
    routing done, no DRC errors
    [FPGA_33_34.kicad_sch, Marble.kicad_sch]
2023-04-17 adding a level translator for I2C_FPGA_SW_RST, no DRC errors
    adding a level translator for I2C_FPGA_SW_RST, no DRC errors
    [FPGA_14_15.kicad_sch, Marble.kicad_sch]
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2023-08-25 changes listed in issue #50 have been made
    changes listed in issue #50 have been made
    [LTM4673.kicad_sch, Marble.kicad_sch, Power_SW.kicad_sch]
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2024-02-28 PCB minor corrections
    [Marble.kicad_sch, Power.kicad_sch]
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2025-02-16 replaced U18, changed version to 1.4.3
    [Marble.kicad_sch]
2025-02-18 Schematic adjustments so fab package can build without errors
    Add one PWR_FLAG to fix an ERC Error
    add Manufacturer and Manufacturer Part Number to U18
    update Manufacturer for U7 and U10
    update a few Manufacturer names for self-consistency
    modify xy_post.py for increased robustness
    [JTAG.kicad_sch, LTM4673.kicad_sch, Marble.kicad_sch, Power.kicad_sch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]
2025-02-19 More version string updates
    Update version listed in schematic to v1.4.3 (24 sheets)
    Update version shown on layout silkscreen to v1.4.3 (3 places)
    Update QR code (and its generating script and instructions) to show
    https://github.com/BerkeleyLab/Marble/releases/tag/v1.4.3
    (but that link won't work until someone tags the release)
    Remove unused Marble.pro file
    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
    [ETH_PHY.kicad_sch, FMC_1.kicad_sch, FMC_2.kicad_sch, FPGA.kicad_sch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]
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2025-03-18 fixed coil symbol issue
    [Power.kicad_sch, USB.kicad_sch]
2025-04-14 clean up some minor lint
    remove the very obsolete design/scripts/72610867-backport.diff
    docs/sphinx/Makefile: convert some tabs to spaces
    design/marble-stack.csv: remove stray Unicode Byte-order mark (BOM)
    Marble_User_Guide.tex: capitalize Pmod correctly
    [marble-stack.csv]
2025-05-08 fixed issue with EN pin of U18; added FB for 3.3P
    [Marble.kicad_sch, Power.kicad_sch]
2025-05-09 Change claimed version to v1.4.4
    Update version listed in schematic to v1.4.4 (24 sheets)
    Update version shown on layout silkscreen to v1.4.4 (3 places)
    https://github.com/BerkeleyLab/Marble/releases/tag/v1.4.4
    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
    [ETH_PHY.kicad_sch, FMC_1.kicad_sch, FMC_2.kicad_sch, FPGA.kicad_sch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]
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
